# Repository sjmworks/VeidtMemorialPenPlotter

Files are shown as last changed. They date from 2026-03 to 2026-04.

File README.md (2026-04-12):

# UQ Multifunctional Composites Syringe Printer

AKA The Viedt Memorial Pen Plotter

By Sam Munro
---

The printer is heavily based upon the work of Jonathan Weiss and the Printess Bio Printer. The head is an exact rip of the Printess extruder setup attached to a fully custom gantry system.

It is suggested that you familiarise yourself with the documentation available on the [Printess GitHub](<https://github.com/weiss-jonathan/Printess-Low-Cost-3D-Printer>) before operating the VMPP.

Feel free to contact Sam - Mitch has my number
## The Printer
The bed size of the printer is 225x285mm. It has two syringe extruder heads. Each head can traverse vertically be 100mm (Z and A axes). The syringes may be depressed 50mm (B and C axes). Printess has a number of additions that can be made to the head which will work on this printer.

X and Y (multistepper in Y) are run by NEMA23 motors and TMC5160T drivers running on SPI. Vert. Axes are Alibaba NEMA17s running on TMC2209 running on UART. Control is run from an OCtopus Pro V1.1 (H723 chip).

Due to the requirement to run on the H723 chip, we are using Marlin 2.1.3-B2 which is a beta debug release of marlin. It is highly recomenned that when the stable release supports the H723 chip that the Firmware is updated to that version.

Currently the printer will home to x_max, y_max. Do not home any of the vert. axis as there are no end stops plugged it. Using sensorless homing is a possible future addition although of limited use as need to me homed manually. It is important to ensure that the vert axes will not crash when previewing the GCode. All other direction limits are software endstops so correct homing of X and Y are critical. The Octopus as 8 pins for endstops however due to the Marlin requirement of having a endstop defined for each axis it is only possible to define a min limit on one axis (one of the extra pins is used for Y2) (this may all be wrong).

The Ocotopus is running seperate power from 24V for logic and motors. The logic circuit will also be powered if you plug in the USBC. When turning on it is important to turn the main power on before connecting via USB C to avoid initialisation errors.

## Before Use and Important Notes

The printer should run both Y motors simutaneously. On occasion, often when homing has not worked properly, only one Y motor will run. If allowed this will damaged the machine. Immeadiatley switch off power (either at the wall or, if installed, on the EStop). This can be fixed by hitting the reset switch on the Octopus (above the USBC port) and rehoming.

It is imoportant to maintain lubrication of the machine both for good operation and to prevent rust. Ball screws and rails will rust if exposed. The rail carts can be lubricated by the screws on the ends. Ensure that the parts of the rails and screws that dont get oiled by movement are regularly sprayed with a lanolin or silicone grease. If parts do become rusty, gently remove with a scotch bright and then relubricate.

Before powering on the machine ensure that the Y Enstops (motor end) are equally space about 5mm from the endplates.

## Suggested Fixes and Improvements
- Estop On Motor Power Input
- The Switch on X_min is currently not used for anything other than decoration. can be wired to V pin easily.
- The Octopus Box needs a lid. DXF file is on USB or in DXF folder on CAD
- Buy and Add Feet to the machine
- 3DP a holder for the bed probe (already owned) and measure flatness of the bed. In initial testing the bed has been flat enough for small parts if you set Z at the centre of your print.
- Some of the screws don't fully engage the Nyloc (sorry). Make sure they stay tight and possibly replace.
- The Y Ball screws should probably be covered for safety
- Sensorless homing on Vertical Axes
- If a problem there is at least one spare endstop switch (V axis)
- lubricant of cart
- 3D printed box kinda sucks. Especially how the usb c doesn't fit

## Marlin and Flashing Firmware to Octopus
The Marlin file is a modified version of the one provided by Printess. Would have been easier to just start from a clean config. Feel free to improve.

The Octopus is currently setup to run over serial from Pronterface. However to flash firmware we use a MicroSD card.

Build from Marlin (ensure the printer isnt connected when building). From the PIO folder, grab firmware.bin and copy onto the SD card (delete firmware.cur if it is already in there). Plug microsd into unpowered octopus and power on over USB C. Wait for status LED to blink as standard, power off usb c and remove SD Card. The file should now be called firmware.cur. You can now power the machine over mains power and replug in the usbc to your computer after the status LED begins blinking.

## Printer Workflow
(note i am writing a lot of this from memory and bad notes after two weeks of Bintangs in Indo so some of the Gcode might be wrong)

Download Pronterface and Cura. Reread the Printess documentation.
Familiarise yourself with typical GCode and coroadinate setups (G90, G91 etc)

Turn on wall power and ensure status LED is blinking before connecting to Laptop over USB C. 

Call G28 X Y to home. Ensure that it backs off from both Y endstops after homing. If not manually move carts off endstops, reset the board via the ocotopus button and try again. ALWAYS CALL 'G28 X Y' as it will attempt to home other motors that do not have endstops if not. Call G90 to set the printer to absolute mode and call "G1 X0 Y0 F600" to send the printer to its start position

Setup Cura as described in Printess Documentation. I have included my Cura configs in the Cura folder but the settings are absolutley not dialled in for any particular reason. The most import thing is to set filament diamater to the internal diameter of your syringe and the extruder diamater to the ID of your chosen syringe. Create a STL of your part. I found it works to set the height as the expected height of the part. you made need to scale in Z in cura to get the correct amount of layers that you desire. Export the STl and bring into Cura and place as you would. Ensure the model sits flush on the build plate. Set up your parameters and slice. This will likely require a signfiicant amount of dialling in to get properties that you are happy with. good job for a RA. Export and save your GCode.

The GCode must be edited before it can be loaded into Pronterface. 
- Delete the Notes at the start
- Delete the notes at the end after the "Time Elapsed" line
- Delete the M104 bed heating commands
- Delete M107 (fans)
- Change the M82 (make sure it is M82 first) to G90. This sets it from extruder relative to total relative since we dont use extruders.
- Delete the "G1 F120 E-3" as we will do this ourselves later
- Use the Find and Replace Feature to change all the "E"s to "B"s. If using multi extruders this might be more complex sorry.

At the end of the GCode Add:
"
G91
G1 B-0.2 F100

G90
G1 Z5 F100
G1 X0 Y0 F400
"
To retract the syringe (if you deleted the extruder pullback in the direct marlin GCode) and to send the machine home

Fill the syringe enusring that no bubbles make it into the nozzle. Place the syringe into the provided holders on the machine. It may be neccessary to call "M18 B" (or other extruder axis) to disasble the stepper so that you can turn the extrusion axis by hand so that you can align the syringe holder with the plunger. Call G28 B0 after you do this. I have been doing a small initialising push in B to prime the nozzle manuallly in the pronterface terminal. If you wish you may add this to the begining of the GCode (before the G28 B0) command. I find 0.3mm of push in B is a good prepressurisation. Make sure there is a G28 B0 somewhere afterwards

Work out where in your build volume you placed the part in Cura (check the GCode against the cura preview). navigate the head to the centre of your part. Place your substrate here. You may need to lift it off the bed to ensure the nozzle can reach. used the most parralell piece of stock you can get your hands on if you need to do this. By hand rotate the Z axis until your syringe just touches the build plate. call "G28 Z0". After this point do not manually spin the Z axis. Call "G1 Z5 F200" to raise the nozzle off the build plate. You should now have set the correct Z height for your part.

When previewing the GCode it is important to preview the Min and Max values (especially for Z as it is homed by hand) to ensure the machine wont crash. go to the last extruion line and check the total change in B (or whatever extrusion axis you are using) and make sure that you fill the syringe to greater than that distance and you have sufficient leadscrew.

Have a final review of the GCode to ensure everything is within bounds and your Z never goes negative. Ensure your Feedrates are sensible. I found for printing around F400 was good. the machine will comfortably rapid X and Y at about F800. The vertical axis should not exceed F300. Test all this.

Load your GCode into the Pronterface using the "load file" button. Check everything again, especially Z heights and that you have correclty called all your G28s especially on Z. Cross your fingers and press print. Stay close to the machine and be ready to shut it down.

Goodluck and happy printing

## Other File
I have included my CAD here as well. It is a bit of a mess admititdley but I do not have Inventor on this Laptop to clean it up so my apologies. Hopefully you can make sense of it.

##

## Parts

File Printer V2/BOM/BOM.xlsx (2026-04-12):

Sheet: Sheet1
Syringe Printer Part List (sans Hardware???)
PART | QTY | MATL | SOURCE | COST PU | COST | Dims Checked? | NOTES | URL
Linear Bearing – HGH15CA | 4 |  | MAKERSTORE | 26.79 | 107.16 | x |  | https://www.makerstore.com.au/product/bear-hgh15ca/
4040 Extrusion | 0.673 |  | MAKERSTORE |  | 30.87 |  | COST IS 1M FROM MAKERSTORE (TAPPED). MANY ALT SOURCES | https://www.makerstore.com.au/product/lr-40-8-4040-s/
4080 EXTRUSION | 0.95 |  | MAKERSTORE |  | 76.04 |  | COST IS 1M FROM MAKERSTORE (TAPPED). MANY ALT SOURCES | https://www.makerstore.com.au/product/lr-40-8-4040-s/
Linear Rail – HGR15 | 0.938 |  | MAKERSTORE |  | 68.09 |  | COST IS 1M FROM MAKERSTORE MANY ALT SOURCES | https://www.makerstore.com.au/product/hard-hgr-15/
SIDE SUPPORT PLATE - MOTOR SIDE | 1 | 6MM ALY | CUT AT UQ. SOURCE ACTION? |  | 0 |  | MAY NEED TO CHANGE Z HEIGHT HERE BASED ON OTHER COMPONENTS
SIDE SUPPORT PLATE - FLOATING SIDE | 1 | 6MM ALY | CUT AT UQ |  | 0
Linear Rail Shaft Guide/SupporT – SHF12 | 4 |  | MAKERSTORE | 4.1 | 16.4 | X |  | https://www.makerstore.com.au/product/brac-shf12/
STEPPER | 3 |  | ? |  | 0 |  | CURRENTLY NEMA 23 NEEDS TO BE SPPECCED
12mm Smooth Rod | 1020 |  | MAKERSTORE | 14.96 | 29.92 |  | 2X 500MM SECTIONS. WILL BE 5MM SHORT EACH SIDE BUT SHOULD BE OK. CAN SPIN THE HOLDER TO OTHER SIDE IF NECESSARY | https://www.makerstore.com.au/product/hard-rod-12/
FF10 Floating Ball Screw Support With Clip | 3 |  | MAKERSTORE | 28.99 | 86.97 | x |  | https://www.makerstore.com.au/product/tr-bs-ff10/
FK10 Fixed Ball Screw Support With Lock Collar | 3 |  | MAKERSTORE | 28.99 | 86.97 | x |  | https://www.makerstore.com.au/product/tr-bs-fk10/
 | 3 |  | MAKERSTORE | 90.04 | 270.12 | X |  | https://www.makerstore.com.au/product/tr-bs-sfu1204/
6.35mm x 8mm Flexible Coupling | 3 |  | MAKERSTORE | 10.24 | 30.72 | x |  | https://www.makerstore.com.au/product/hard-coup-635x8/
Linear Bearing Block – 12mm – SCS12UU | 4 |  | MAKERSTORE | 6.22 | 24.88 | X |  | https://www.makerstore.com.au/product/bear-scs12uu/
DSG12H Ball Nut Housing | 1 |  | MAKERSTORE | 23.63 | 23.63 |  |  | https://www.makerstore.com.au/product/tr-bs-dsg12/
X Plate |  | 6MM ALY | CUT AT UQ |  | 0
END PLATE FIXED SIDE | 2 | 6MM ALY | CUT AT UQ |  | 0
END PLATE MOTOR SIDE | 2 | 6MM ALY | CUT AT UQ |  | 0
TOOL PLATE |  | ? |  |  | 0
ALIEXPRESS 50 AND 100MM LINEAR THINGS |  | 3DP |  |  | 0
Z AXES HOLDER | 2 | 3DP | UQ |  | 0
PLUNGER HOLDERS |  |  |  |  | 0
SYRINGES |  |  |  |  | 0
SYRINGE TIPS |  |  |  |  | 0
PSU |  |  |  |  | 0
2 Hole Corner Bracket – 40 Series | 8 |  | MAKERSTORE | 3.15 | 25.2 |  |  | https://www.makerstore.com.au/product/brac-40s-90cast-b/
 |  |  |  |  | 851.77
 |  |  |  |  | 0
 |  |  |  |  | 0
 |  |  |  |  | 0
 |  |  |  |  | 0
 |  |  |  |  | 0
 |  |  |  |  | 0
 |  |  |  |  | 0
 |  |  |  |  | 0
 |  |  |  |  | 0

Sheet: Sheet2
0.005
0.02

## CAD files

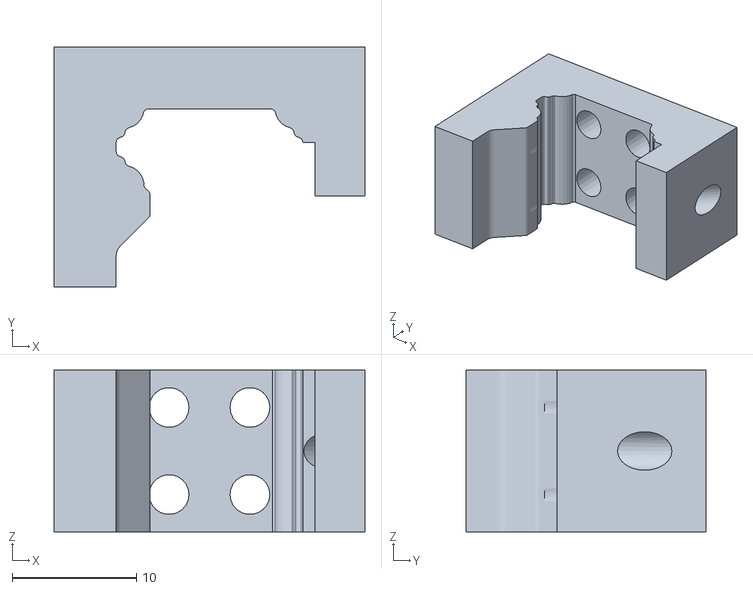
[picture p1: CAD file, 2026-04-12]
Printer V2/3D Printing/QTY4- HGR_LIMITSWITCHHOLDERv2.stl
25.0 x 19.3 x 13.0

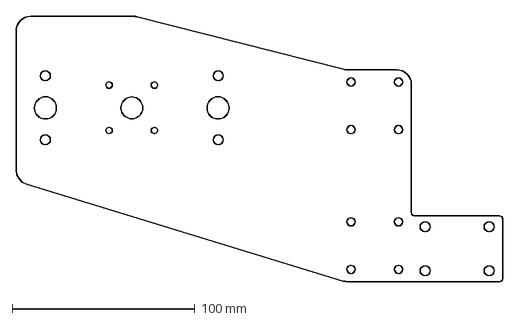
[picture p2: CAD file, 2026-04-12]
Printer V2/DWG/LASER CUTTING - DXFS/QTY 1 - SIDE SUPPORT PLATE - PASSIVE SIDE.dxf
266.0 x 145.0 mm

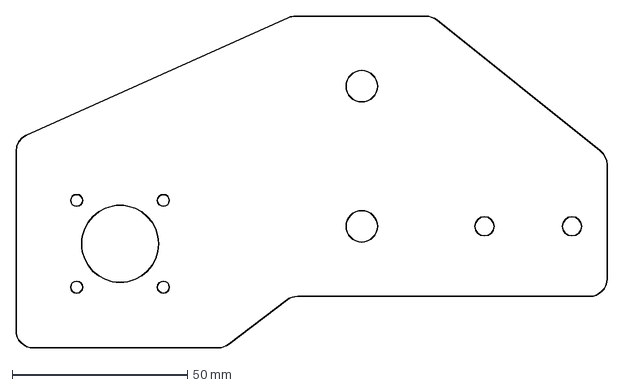
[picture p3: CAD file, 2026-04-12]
Printer V2/DWG/LASER CUTTING - FOR QUOTE/LASER CUTTING - DXFS/QTY 2 - ENDPLATE - PASSIVE SIDE.dxf
168.7 x 94.7 mm

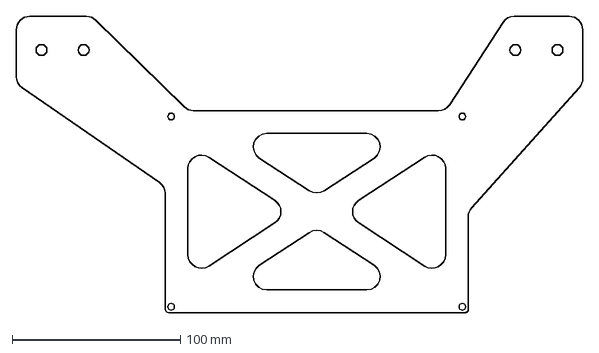
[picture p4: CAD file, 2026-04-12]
Printer V2/DXFS/ocotpous_box_backing plate.dxf
336.5 x 176.0 mm

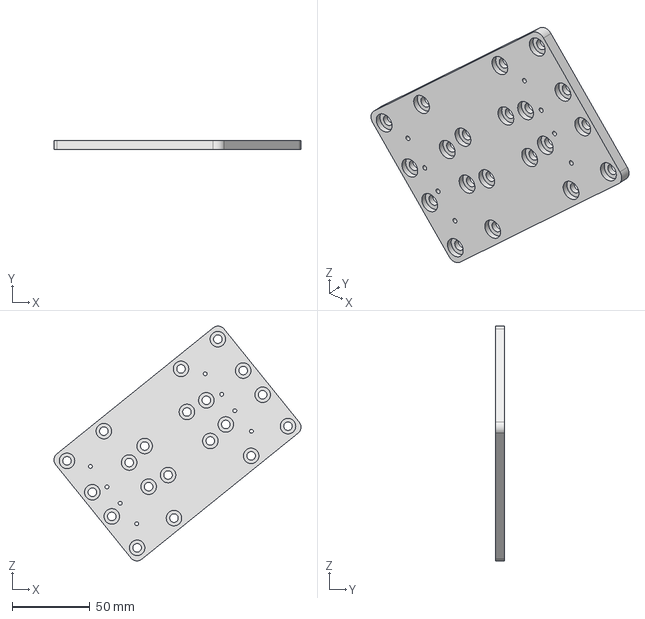
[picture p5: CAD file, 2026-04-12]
Printer V2/FOR MACHINING/X_PLATE.stp
159.2 x 6.00 x 151.3 mm

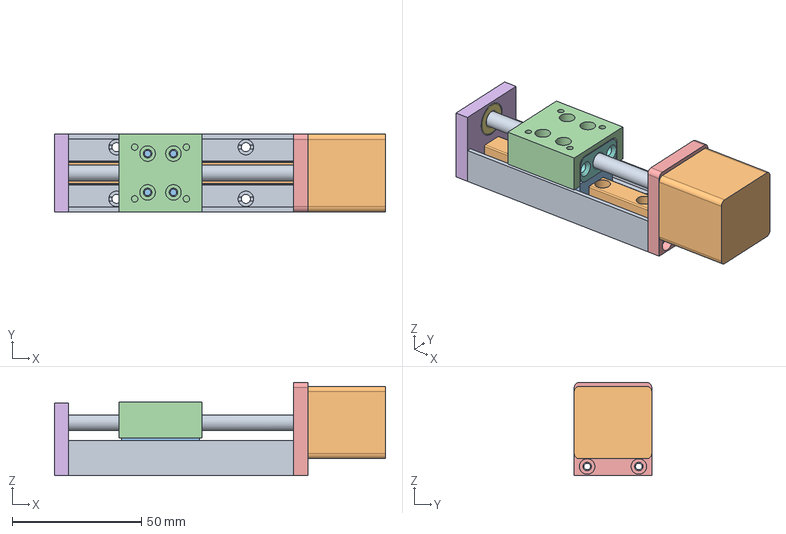
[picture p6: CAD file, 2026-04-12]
Printer V2/PRINTESS FILES/DG281-50L .stp
128.0 x 30.0 x 36.0 mm

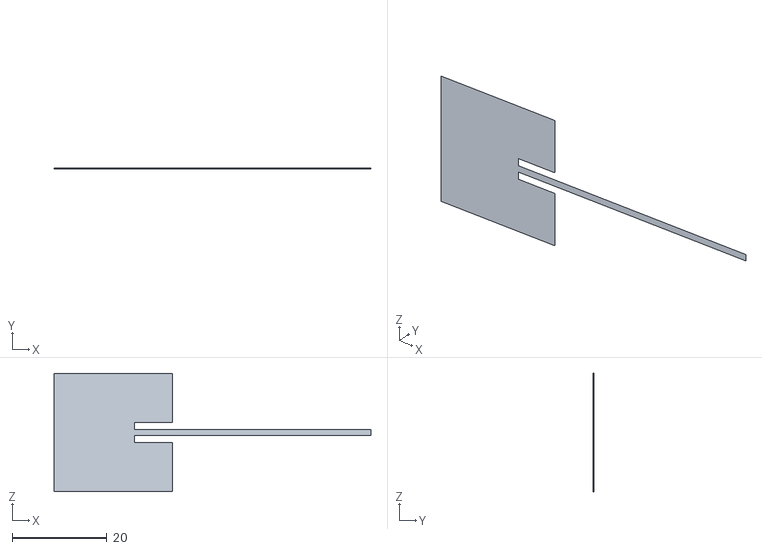
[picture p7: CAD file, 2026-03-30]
Printer V2/PRINTING FILES/TESTPRINT1_1.stl
67.0 x 0.1 x 25.0

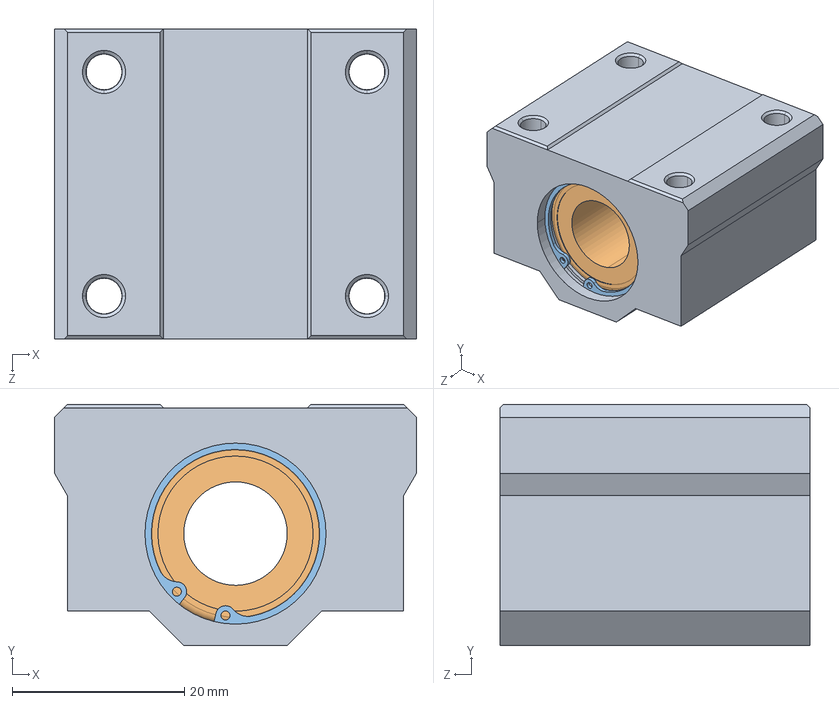
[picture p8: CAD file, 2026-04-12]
Printer V2/SCS12UU.STEP
42.0 x 28.0 x 36.0 mm
3_PreviewCfg x 2

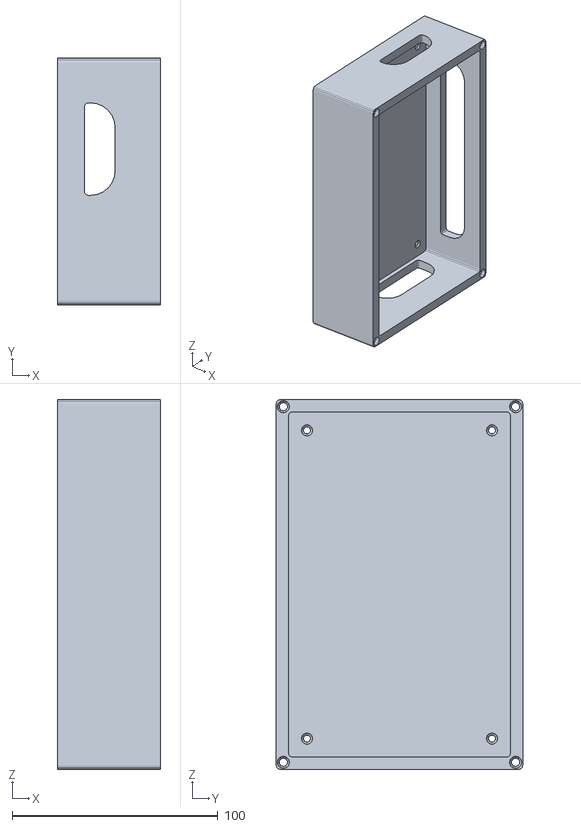
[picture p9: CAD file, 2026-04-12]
Printer V2/3D Printing/OCTOPUS_BOX.stl
50.0 x 120.0 x 180.0

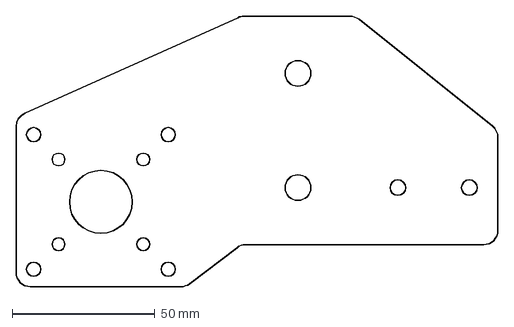
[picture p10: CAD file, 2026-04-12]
Printer V2/DWG/LASER CUTTING - DXFS/QTY 2 - ENDPLATE - MOTOR SIDE.dxf
168.7 x 94.7 mm

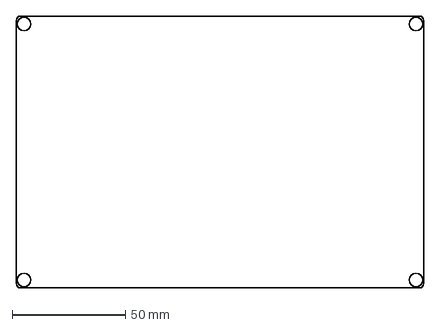
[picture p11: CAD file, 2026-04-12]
Printer V2/DXFS/ocotppusbox lid.dxf
180.0 x 120.0 mm

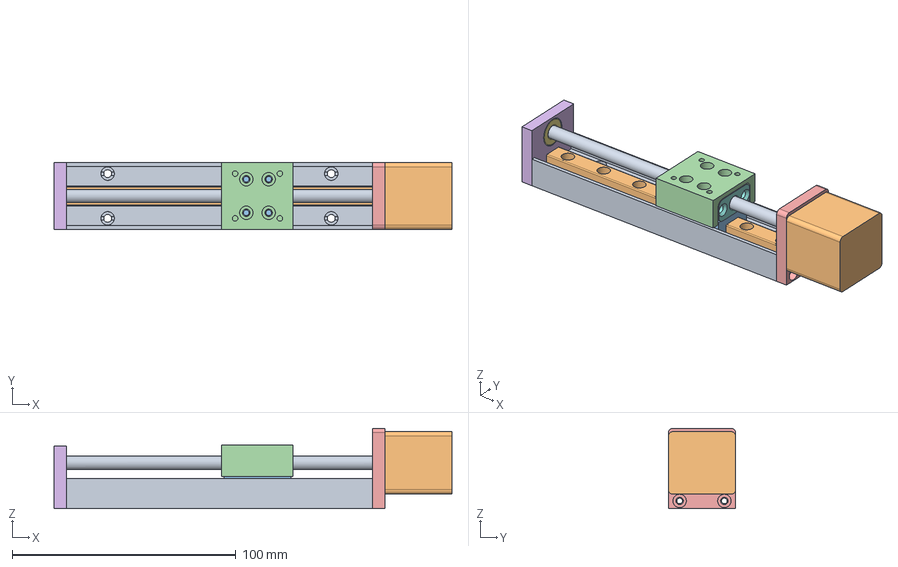
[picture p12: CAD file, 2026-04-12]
Printer V2/PRINTESS FILES/DG281-100L .stp
178.0 x 30.0 x 36.0 mm

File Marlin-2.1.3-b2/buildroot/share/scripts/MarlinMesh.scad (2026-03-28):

 /**************************************\
 *                                      *
 *   OpenSCAD Mesh Display              *
 *   by Thinkyhead - April 2017         *
 *                                      *
 *   Copy the grid output from Marlin,  *
 *   paste below as shown, and use      *
 *   OpenSCAD to see a visualization    *
 *   of your mesh.                      *
 *                                      *
 \**************************************/

$t = 0.15; // comment out during animation!
X = 0; Y = 1;
L = 0; R = 1; F = 2; B = 3;

//
// Sample Mesh - Replace with your own
//
measured_z = [
  [ -1.20, -1.13, -1.09, -1.03, -1.19 ],
  [ -1.16, -1.25, -1.27, -1.25, -1.08 ],
  [ -1.13, -1.26, -1.39, -1.31, -1.18 ],
  [ -1.09, -1.20, -1.26, -1.21, -1.18 ],
  [ -1.13, -0.99, -1.03, -1.06, -1.32 ]
];

//
// An offset to add to all points in the mesh
//
zadjust     = 0;

//
// Mesh characteristics
//
bed_size = [ 200, 200 ];

mesh_inset  = [ 10, 10, 10, 10 ]; // L, F, R, B

mesh_bounds = [
  [ mesh_inset[L], mesh_inset[F] ],
  [ bed_size[X] - mesh_inset[R], bed_size[Y] - mesh_inset[B] ]
];

mesh_size = mesh_bounds[1] - mesh_bounds[0];

                      // NOTE: Marlin meshes already subtract the probe offset
NAN         = 0;      // Z to use for un-measured points

//
// Geometry
//

max_z_scale   = 100;   // Scale at Time 0.5
min_z_scale   = 10;    // Scale at Time 0.0 and 1.0
thickness     = 0.5;   // thickness of the mesh triangles
tesselation   = 1;     // levels of tesselation from 0-2
alternation   = 2;     // direction change modulus (try it)

//
// Appearance
//

show_plane    = true;
show_labels   = true;
show_coords   = true;
arrow_length  = 5;

label_font_lg = "Arial";
label_font_sm = "Arial";
mesh_color    = [1,1,1,0.5];
plane_color   = [0.4,0.6,0.9,0.6];

//================================================ Derive useful values

big_z = max_2D(measured_z,0);
lil_z = min_2D(measured_z,0);

mean_value = (big_z + lil_z) / 2.0;

mesh_points_y = len(measured_z);
mesh_points_x = len(measured_z[0]);

xspace = mesh_size[X] / (mesh_points_x - 1);
yspace = mesh_size[Y] / (mesh_points_y - 1);

// At $t=0 and $t=1 scale will be 100%
z_scale_factor = min_z_scale + (($t > 0.5) ? 1.0 - $t : $t) * (max_z_scale - min_z_scale) * 2;

//
// Min and max recursive functions for 1D and 2D arrays
// Return the smallest or largest value in the array
//
function some_1D(b,i) = (i<len(b)-1) ? (b[i] && some_1D(b,i+1)) : b[i] != 0;
function some_2D(a,j) = (j<len(a)-1) ? some_2D(a,j+1) : some_1D(a[j], 0);
function min_1D(b,i) = (i<len(b)-1) ? min(b[i], min_1D(b,i+1)) : b[i];
function min_2D(a,j) = (j<len(a)-1) ? min_2D(a,j+1) : min_1D(a[j], 0);
function max_1D(b,i) = (i<len(b)-1) ? max(b[i], max_1D(b,i+1)) : b[i];
function max_2D(a,j) = (j<len(a)-1) ? max_2D(a,j+1) : max_1D(a[j], 0);

//
// Get the corner probe points of a grid square.
//
// Input  : x,y grid indexes
// Output : An array of the 4 corner points
//
function grid_square(x,y) = [
  [x * xspace, y * yspace, z_scale_factor * (measured_z[y][x] - mean_value)],
  [x * xspace, (y+1) * yspace, z_scale_factor * (measured_z[y+1][x] - mean_value)],
  [(x+1) * xspace, (y+1) * yspace, z_scale_factor * (measured_z[y+1][x+1] - mean_value)],
  [(x+1) * xspace, y * yspace, z_scale_factor * (measured_z[y][x+1] - mean_value)]
];

// The corner point of a grid square with Z centered on the mean
function pos(x,y,z) = [x * xspace, y * yspace, z_scale_factor * (z - mean_value)];

//
// Draw the point markers and labels
//
module point_markers(show_home=true) {
  // Mark the home position 0,0
  if (show_home)
    translate([1,1]) color([0,0,0,0.25])
      cylinder(r=1, h=z_scale_factor, center=true);

  for (x=[0:mesh_points_x-1], y=[0:mesh_points_y-1]) {
    z = measured_z[y][x] - zadjust;
    down = z < mean_value;
    xyz = pos(x, y, z);
    translate([ xyz[0], xyz[1] ]) {

      // Show the XY as well as the Z!
      if (show_coords) {
        color("black")
        translate([0,0,0.5]) {
          $fn=8;
          rotate([0,0]) {
            posx = floor(mesh_bounds[0][X] + x * xspace);
            posy = floor(mesh_bounds[0][Y] + y * yspace);
            text(str(posx, ",", posy), 2, label_font_sm, halign="center", valign="center");
          }
        }
      }

      translate([ 0, 0, xyz[2] ]) {
        // Label each point with the Z
        v = z - mean_value;
        if (show_labels) {

          color(abs(v) < 0.1 ? [0,0.5,0] : [0.25,0,0])
          translate([0,0,down?-10:10]) {

            $fn=8;
            rotate([90,0])
              text(str(z), 6, label_font_lg, halign="center", valign="center");

            if (v)
              translate([0,0,down?-6:6]) rotate([90,0])
                text(str(down || !v ? "" : "+", v), 3, label_font_sm, halign="center", valign="center");
          }
        }

        // Show an arrow pointing up or down
        if (v) {
          rotate([0, down ? 180 : 0]) translate([0,0,-1])
            cylinder(
              r1=0.5,
              r2=0.1,
              h=arrow_length, $fn=12, center=1
            );
        }
        else
          color([1,0,1,0.4]) sphere(r=1.0, $fn=20, center=1);
      }
    }
  }
}

//
// Split a square on the diagonal into
// two triangles and render them.
//
//     s : a square
//   alt : a flag to split on the other diagonal
//
module tesselated_square(s, alt=false) {
  add = [0,0,thickness];
  p1 = [
    s[0], s[1], s[2], s[3],
    s[0]+add, s[1]+add, s[2]+add, s[3]+add
  ];
  f1 = alt
      ? [ [0,1,3], [4,5,1,0], [4,7,5], [5,7,3,1], [7,4,0,3] ]
      : [ [0,1,2], [4,5,1,0], [4,6,5], [5,6,2,1], [6,4,0,2] ];
  f2 = alt
      ? [ [1,2,3], [5,6,2,1], [5,6,7], [6,7,3,2], [7,5,1,3] ]
      : [ [0,2,3], [4,6,2,0], [4,7,6], [6,7,3,2], [7,4,0,3] ];

  // Use the other diagonal
  polyhedron(points=p1, faces=f1);
  polyhedron(points=p1, faces=f2);
}

/**
 * The simplest mesh display
 */
module simple_mesh(show_plane=show_plane) {
  if (show_plane) color(plane_color) cube([mesh_size[X], mesh_size[Y], thickness]);
  color(mesh_color)
    for (x=[0:mesh_points_x-2], y=[0:mesh_points_y-2])
      tesselated_square(grid_square(x, y));
}

/**
 * Subdivide the mesh into smaller squares.
 */
module bilinear_mesh(show_plane=show_plane,tesselation=tesselation) {
  if (show_plane) color(plane_color) translate([-5,-5]) cube([mesh_size[X]+10, mesh_size[Y]+10, thickness]);

  if (some_2D(measured_z, 0)) {

    tesselation = tesselation % 4;
    color(mesh_color)
    for (x=[0:mesh_points_x-2], y=[0:mesh_points_y-2]) {
      square = grid_square(x, y);
      if (tesselation < 1) {
        tesselated_square(square,(x%alternation)-(y%alternation));
      }
      else {
        subdiv_4 = subdivided_square(square);
        if (tesselation < 2) {
          for (i=[0:3]) tesselated_square(subdiv_4[i],i%alternation);
        }
        else {
          for (i=[0:3]) {
            subdiv_16 = subdivided_square(subdiv_4[i]);
            if (tesselation < 3) {
              for (j=[0:3]) tesselated_square(subdiv_16[j],j%alternation);
            }
            else {
              for (j=[0:3]) {
                subdiv_64 = subdivided_square(subdiv_16[j]);
                if (tesselation < 4) {
                  for (k=[0:3]) tesselated_square(subdiv_64[k]);
                }
              }
            }
          }
        }
      }
    }

  }
}

//
// Subdivision helpers
//
function ctrz(a) = (a[0][2]+a[1][2]+a[3][2]+a[2][2])/4;
function avgx(a,i) = (a[i][0]+a[(i+1)%4][0])/2;
function avgy(a,i) = (a[i][1]+a[(i+1)%4][1])/2;
function avgz(a,i) = (a[i][2]+a[(i+1)%4][2])/2;

//
// Convert one square into 4, applying bilinear averaging
//
// Input  : 1 square (4 points)
// Output : An array of 4 squares
//
function subdivided_square(a) = [
  [ // SW square
    a[0],                          // SW
    [a[0][0],avgy(a,0),avgz(a,0)], // CW
    [avgx(a,1),avgy(a,0),ctrz(a)], // CC
    [avgx(a,1),a[0][1],avgz(a,3)]  // SC
  ],
  [ // NW square
    [a[0][0],avgy(a,0),avgz(a,0)], // CW
    a[1],                          // NW
    [avgx(a,1),a[1][1],avgz(a,1)], // NC
    [avgx(a,1),avgy(a,0),ctrz(a)]  // CC
  ],
  [ // NE square
    [avgx(a,1),avgy(a,0),ctrz(a)], // CC
    [avgx(a,1),a[1][1],avgz(a,1)], // NC
    a[2],                          // NE
    [a[2][0],avgy(a,0),avgz(a,2)]  // CE
  ],
  [ // SE square
    [avgx(a,1),a[0][1],avgz(a,3)], // SC
    [avgx(a,1),avgy(a,0),ctrz(a)], // CC
    [a[2][0],avgy(a,0),avgz(a,2)], // CE
    a[3]                           // SE
  ]
];


//================================================ Run the plan

translate([-mesh_size[X] / 2, -mesh_size[Y] / 2]) {
  $fn = 12;
  point_markers();
  bilinear_mesh();
}

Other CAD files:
Printer V2/DWG/ENDPLATES - DWG.dwg
Printer V2/DWG/UQ Composites - Sami.dwg
Printer V2/FOR MACHINING/X PLATE - DWG.dwg
Printer V2/PRINTING FILES/TESTPRINT1.stl
Printer V2/12MM_X_AXIS_SHAFT.ipt
Printer V2/178202343-9-stepper_am23hs0420-01/OldVersions/stepper_am23hs0420-01.0001.iam
Printer V2/178202343-9-stepper_am23hs0420-01/OldVersions/stepper_am23hs0420-01_01.0001.ipt
Printer V2/178202343-9-stepper_am23hs0420-01/OldVersions/stepper_am23hs0420-01_02.0001.ipt
Printer V2/178202343-9-stepper_am23hs0420-01/stepper_am23hs0420-01.iam
Printer V2/178202343-9-stepper_am23hs0420-01/stepper_am23hs0420-01_01.ipt
Printer V2/178202343-9-stepper_am23hs0420-01/stepper_am23hs0420-01_02.ipt
Printer V2/3D Printing/QTY 2 1mL Barrel Holder.stl
Printer V2/3D Printing/QTY 2 1mL Plunger Holder.stl
Printer V2/3D Printing/QTY 2 5mL BD Plunger Holder.stl
Printer V2/3D Printing/QTY 2 5mL Barrel Holder.stl
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

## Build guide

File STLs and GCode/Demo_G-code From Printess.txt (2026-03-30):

; Demo GCode for a 2-syringe multimaterial print.

; Clear Nozzle Extrusion Coefficient = 2
G90 ; Absolute mode
G21 ; Set units to mm

; Manually position all axes to desired starting position. Bring nozzles so that they just barely make contact with the stage

G1 X0 Y0 Z2 A2 F300 ; Move nozzles up so they don't crash into the print
G1 Z0.05 F200 ; Move Z nozzle up a defined height for extrusion. ADJUST IF NECESSARY

;;;;;;;;;;;;;;;;;;;;;;;;;;;;;;;;;;;;;;;;;;;;;;;;;;;;;;;;;;;;;;;;;;;;;;;;;;;;;;
G91; Relative mode
G1 B0.1 F200 ; WRITE IN the initial distance to pressurize the syringe
G92 B0; Set extruder position to 0 after initial pressurization
;;;;;;;;;;;;;;;;;;;;;;;;;;;;;;;;;;;;;;;;;;;;;;;;;;;;;;;;;;;;;;;;;;;;;;;;;;;;;;

G90 ; absolute mode

G1 X5.3 Y0.0 B0.025 F300.0
G1 X5.3 Y0.5 B0.027 F300.0
G1 X0.0 Y0.5 B0.052 F300.0
G1 X0.0 Y1.0 B0.055 F300.0
G1 X5.3 Y1.0 B0.08 F300.0
G1 X5.3 Y1.5 B0.082 F300.0
G1 X0.0 Y1.5 B0.107 F300.0
G1 X0.0 Y2.0 B0.11 F300.0
G1 X5.3 Y2.0 B0.135 F300.0
G1 X5.3 Y2.5 B0.137 F300.0
G1 X0.0 Y2.5 B0.162 F300.0
G1 X0.0 Y3.0 B0.164 F300.0
G1 X5.3 Y3.0 B0.19 F300.0
G1 X5.3 Y3.5 B0.192 F300.0
G1 X0.0 Y3.5 B0.217 F300.0
G1 X0.0 Y4.0 B0.219 F300.0
G1 X5.3 Y4.0 B0.244 F300.0
G1 X5.3 Y4.5 B0.247 F300.0
G1 X0.0 Y4.5 B0.272 F300.0
G1 X0.0 Y5.0 B0.274 F300.0
G1 X5.3 Y5.0 B0.299 F300.0

;;;;;;;;;;;;;;;;;;;;;;;;;;;;;;;;;;;;;;;;;;;;;;;;;;;;;;;;;;;;;;;;;;;;;;;;;;;;;;
G91
G1 B-0.1 F200; WRITE in the distance to depressurize the syringe
G92 B0 ; Reset Extruder to 0
;;;;;;;;;;;;;;;;;;;;;;;;;;;;;;;;;;;;;;;;;;;;;;;;;;;;;;;;;;;;;;;;;;;;;;;;;;;;;;

G90
G1 Z1.0 F300.0; Raise Z to get out of the way of the print.

;;;;;;;;;;;;;;;Adjust for X/Y Offset between plungers;;;;;;;;;;;;;;
G91
G1 X32.67 Y0.55 F300.0
G92 X0 Y0
;;;;;;;;;;;;;;;;;;;;;;;;;;;;;;;;;;;;;;;;;;;;;;;;;;;;;;;;;;;;;;;;;;;

G90
G1 X0 Y0 A0.05 F300; Bring A axis down

;;;;;;;;;;;;;;;;;;;;;;;;;;;;;;;;;;;;;;;;;;;;;;;;;;;;;;;;;;;;;;;;;;;;;;;;;;;;;;
G91
G1 C0.1 F200 ; WRITE IN the distance to pressurize the syringe 
G92 C0 ; DEFINE EXTRUDER POSITION TO MATCH THE BEGINNING OF THE EXTRUSION VALUES BELOW
;;;;;;;;;;;;;;;;;;;;;;;;;;;;;;;;;;;;;;;;;;;;;;;;;;;;;;;;;;;;;;;;;;;;;;;;;;;;;;

G90

G1 X0.0 Y-5.1 C0.024 F300.0
G1 X-0.5 Y-5.1 C0.026 F300.0
G1 X-0.5 Y0.0 C0.051 F300.0
G1 X-1.0 Y0.0 C0.053 F300.0
G1 X-1.0 Y-5.1 C0.077 F300.0
G1 X-1.5 Y-5.1 C0.079 F300.0
G1 X-1.5 Y0.0 C0.103 F300.0
G1 X-2.0 Y0.0 C0.106 F300.0
G1 X-2.0 Y-5.1 C0.13 F300.0
G1 X-2.5 Y-5.1 C0.132 F300.0
G1 X-2.5 Y0.0 C0.156 F300.0
G1 X-3.0 Y0.0 C0.159 F300.0
G1 X-3.0 Y-5.1 C0.183 F300.0
G1 X-3.5 Y-5.1 C0.185 F300.0
G1 X-3.5 Y0.0 C0.209 F300.0
G1 X-4.0 Y0.0 C0.212 F300.0
G1 X-4.0 Y-5.1 C0.236 F300.0
G1 X-4.5 Y-5.1 C0.238 F300.0
G1 X-4.5 Y0.0 C0.262 F300.0
G1 X-5.0 Y0.0 C0.265 F300.0
G1 X-5.0 Y-5.1 C0.289 F300.0

;;;;;;;;;;;;;;;;;;;;;;;;;;;;;;;;;;;;;;;;;;;;;;;;;;;;;;;;;;;;;;;;;;;;;;;;;;;;;;
G91
G1 C-0.1 F200; WRITE IN the distance to depressurize the syringe
;;;;;;;;;;;;;;;;;;;;;;;;;;;;;;;;;;;;;;;;;;;;;;;;;;;;;;;;;;;;;;;;;;;;;;;;;;;;;;

G90
G1 X-40 Y-5.1 Z10 A10 F300
G92 X0 Y0 Z10 A10 ;Reset coordinates ready for next print to the side

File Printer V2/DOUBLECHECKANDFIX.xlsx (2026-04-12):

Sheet: Sheet1
QUESTIONS TO FIX DON’T FORGET | NOTES | CHECKED?
ACTUAL BASE DIMESNIONS | WILL BE DRIVEN BY GANTRY AND PART OVERHANGS TO HIT TARGET WORKSIZE
ROUIND SHAFT MOUNTAIN HOLES SEP DIST | CURRENTLY SIZED FOR THE MAKERSTORE PARTS
NEMA MOTOR MOUNTINA HOLE SPACING
CENTRE HOLE FOR BALL SCREW MOUNTINA
MIUNTAIN PLATE FORWARD AND BACK DIST
CART DEPERATION
NEMA SIZING
LINEAR SHAFT HOLE SIZE FOR CUTTING
THICKNESS OF ENDPLATES
z HEIGHT | MITCH QUESTION
TYPE AND QUAlity of linear BEARING BLOCK
FROM ABOVE - HOLE SIZING
YAXIS CART HOLE SIZING
YAXIS CARTS MATCH PURCHASED UNITS
MOUNT FIXED END ON INSIDE OR OUTSIDE
SPEC MOTORS
X MOTOR STANDOFF DISTANCE
RPD END TINGS ARE NOT TO SPEC OF MAKERSTORE
Limit switches
OUTBOARDSPACING OF Y SCREW
STANDOFF Y AXIS FK TO ADD PLAY |  |  |  | 23
Holes in rail
 |  |  | 960
https://kiwimotion.co.uk/technical-articles/ball-screws/ball-screw-selection/ |  |  | 640
https://m.media-amazon.com/images/I/71zBOVmqRrL._UF1000,1000_QL80_.jpg |  |  | 436

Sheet: CALCS
4080 |  |  | 12MM ROD
sa | 15.332 | CM2 | SA | 1.130973355 | CM2
VOL/M | 1533.2 | CM3 | VOL/M | 113.0973355 | CM3
DENSITY | 2.7 | G/CM3 | DENSITY | 7.8 | G/CM3
MASS/M | 4139.64 | G | MASS/M | 882.1592171 | G/CM3
2040
sa | 2.75
VOL/M | 275
DENSITY | 2.7
MASS/M | 742.5

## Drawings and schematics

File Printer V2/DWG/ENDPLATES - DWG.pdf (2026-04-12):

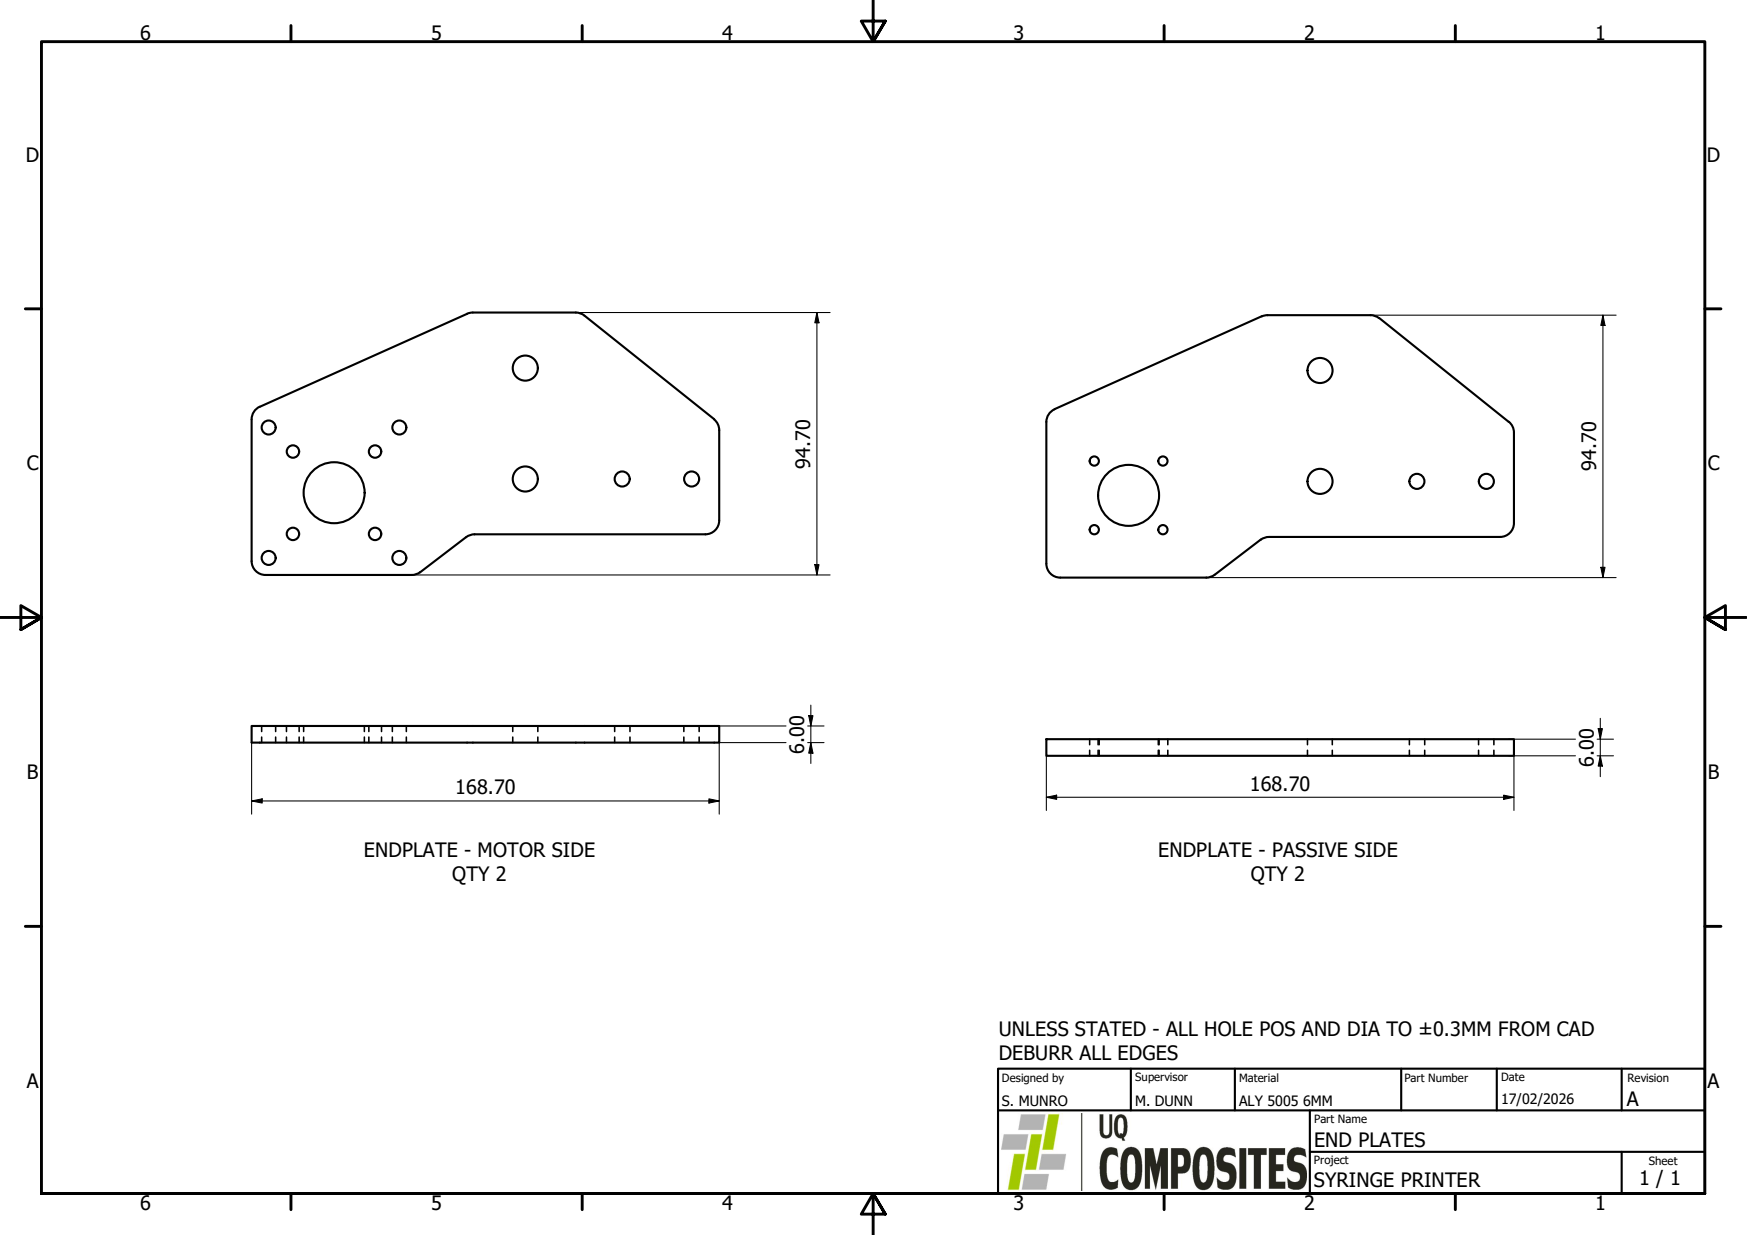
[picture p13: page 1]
QTY 2

ENDPLATE - MOTOR SIDE

ENDPLATE - PASSIVE SIDE

UNLESS STATED - ALL HOLE POS AND DIA TO ±0.3MM FROM CAD
DEBURR ALL EDGES

Designed by S. MUNRO | Supervisor M. DUNN | Material ALY 5005 6MM | Part Number | Date 17/02/2026 | Revision A

Part Name END PLATES

Project SYRINGE PRINTER | Sheet 1 / 1

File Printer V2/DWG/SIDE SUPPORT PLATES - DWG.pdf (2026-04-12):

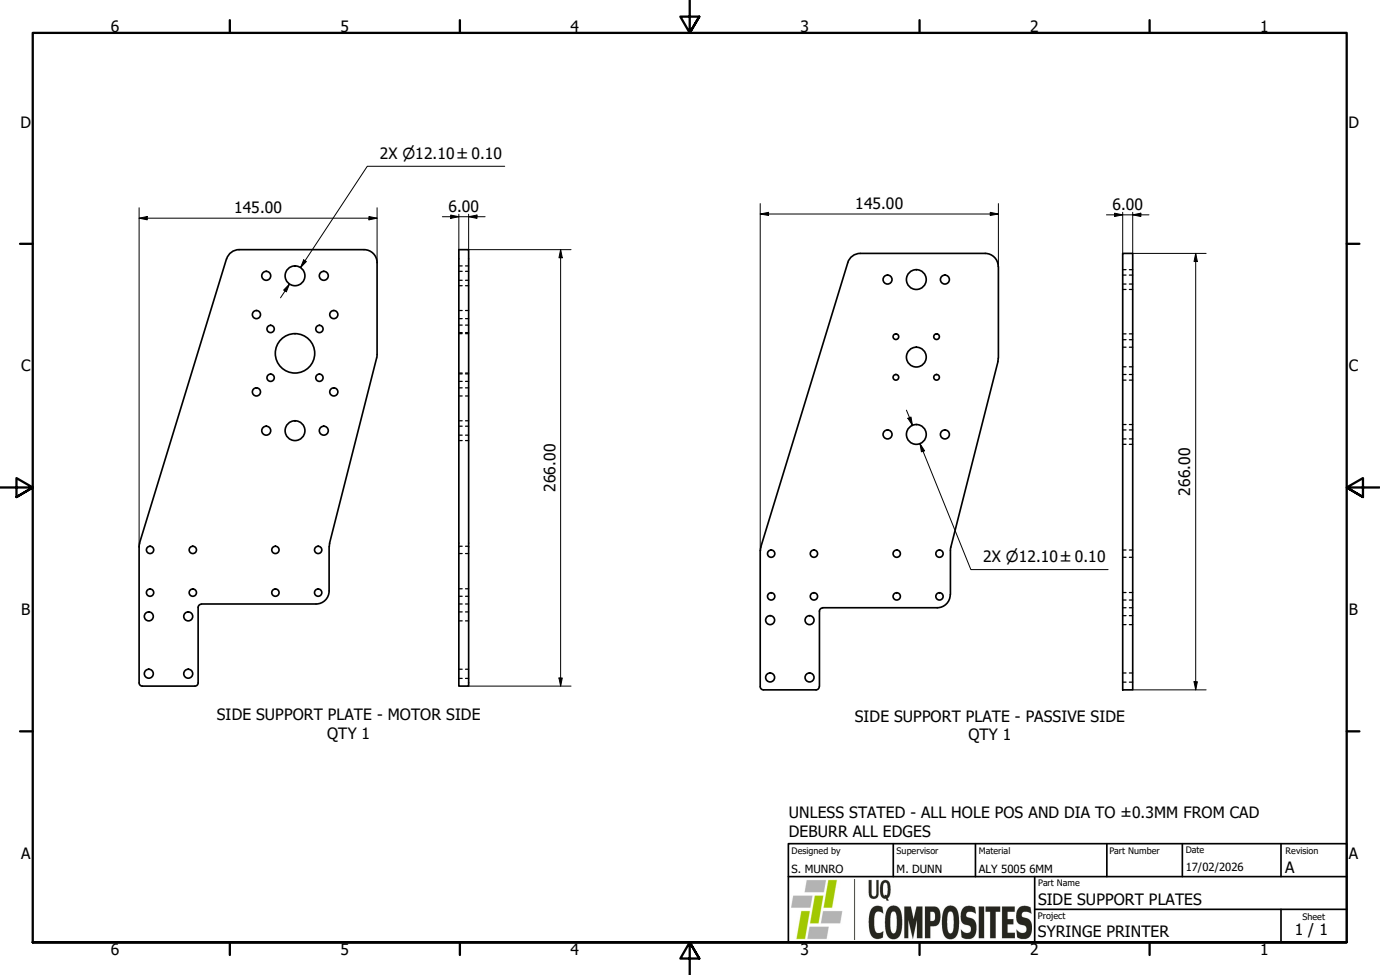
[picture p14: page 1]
QTY 1

SIDE SUPPORT PLATE - MOTOR SIDE

SIDE SUPPORT PLATE - PASSIVE SIDE

UNLESS STATED - ALL HOLE POS AND DIA TO ±0.3MM FROM CAD
DEBURR ALL EDGES

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

Part Name SIDE SUPPORT PLATES

Project SYRINGE PRINTER | Sheet 1 / 1

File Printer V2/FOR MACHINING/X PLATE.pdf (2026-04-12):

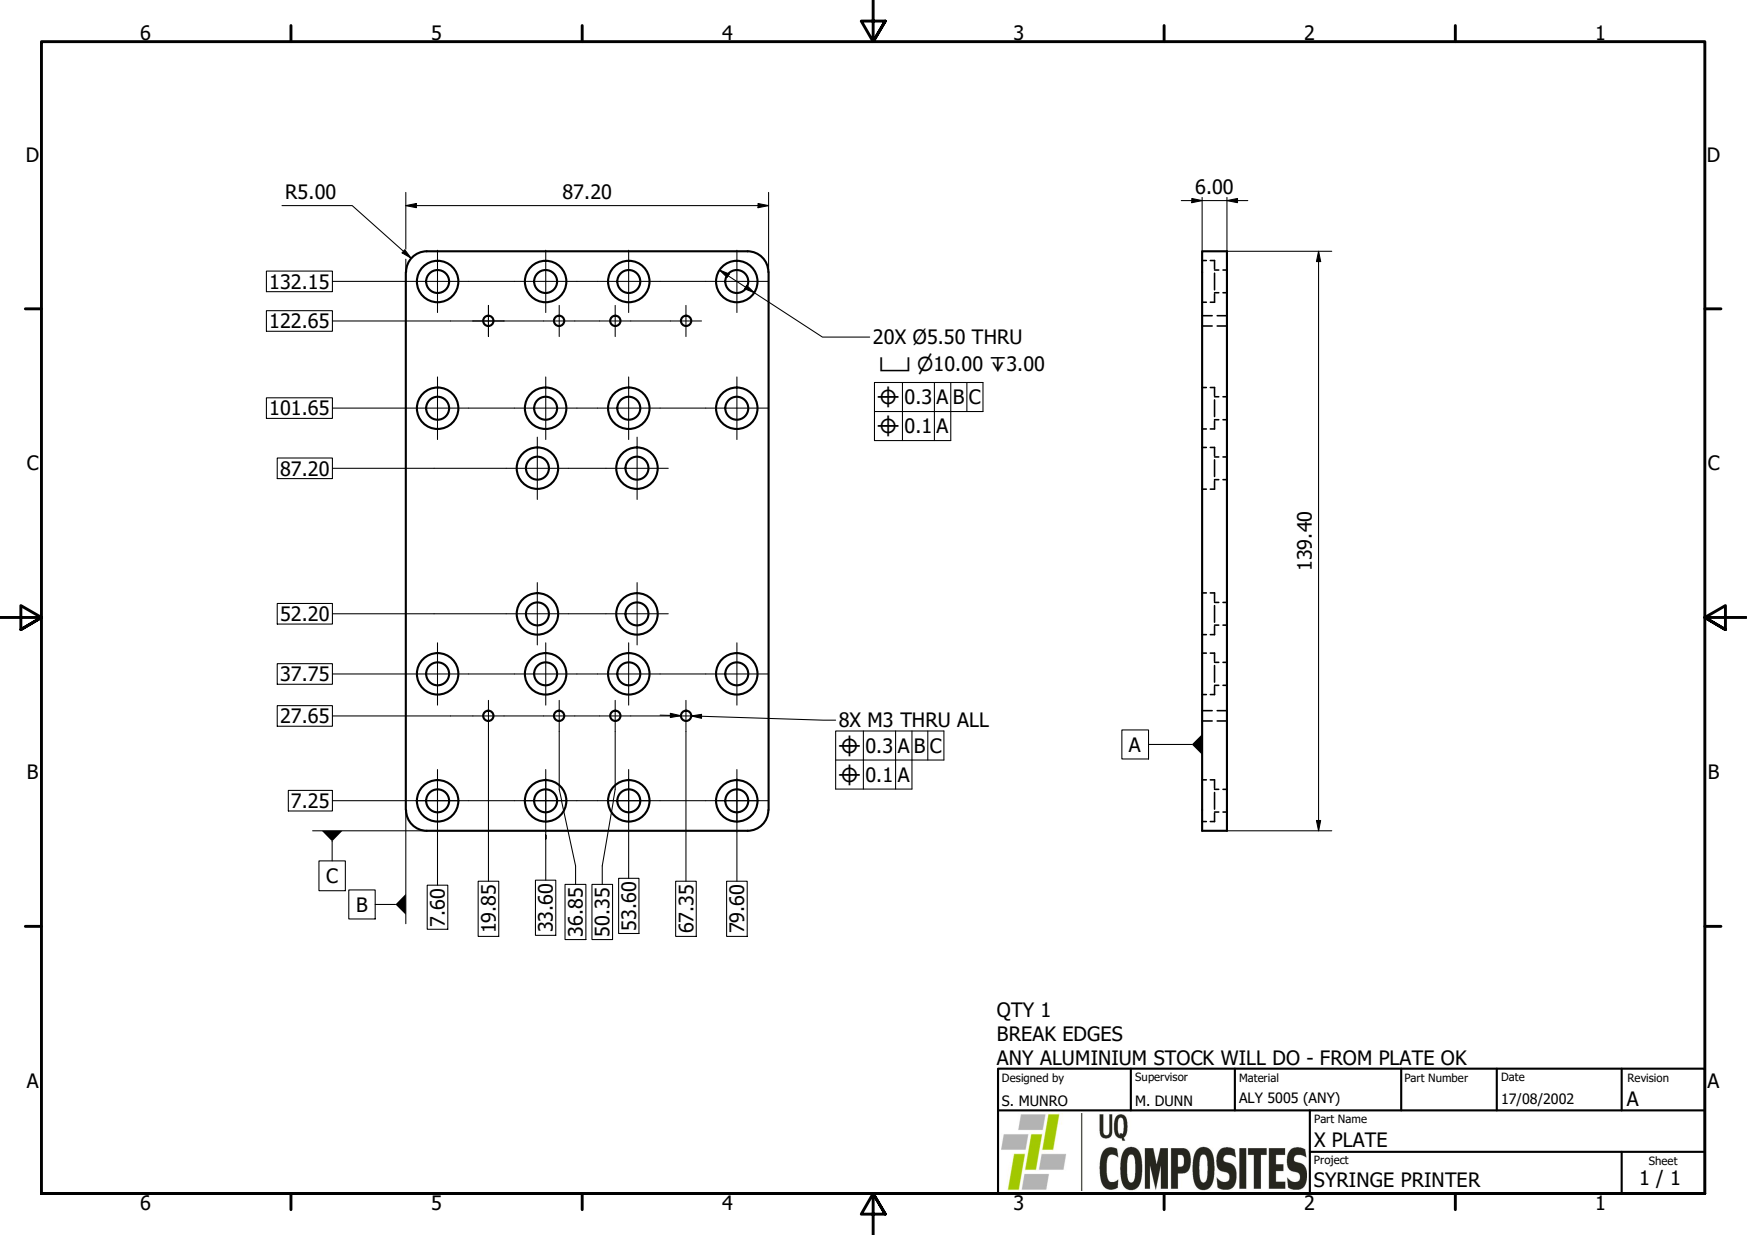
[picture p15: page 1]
20X Ø5.50 THRU; 8X M3 THRU ALL ⌖ 0.3 A B C

⌖ 0.3 A B C
⌖ 0.1 A

QTY 1
BREAK EDGES
ANY ALUMINIUM STOCK WILL DO - FROM PLATE OK

Designed by S. MUNRO | Supervisor M. DUNN | Material ALY 5005 (ANY) | Part Number | Date 17/08/2002 | Revision A

Part Name X PLATE

Project SYRINGE PRINTER | Sheet 1 / 1

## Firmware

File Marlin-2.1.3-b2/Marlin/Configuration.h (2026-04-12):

/**
 * Marlin 3D Printer Firmware
 * Copyright (c) 2020 MarlinFirmware [https://github.com/MarlinFirmware/Marlin]
 *
 * Based on Sprinter and grbl.
 * Copyright (c) 2011 Camiel Gubbels / Erik van der Zalm
 *
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
 */
#pragma once

/**
 * Configuration.h
 *
 * Basic settings such as:
 *
 * - Type of electronics
 * - Type of temperature sensor
 * - Printer geometry
 * - Endstop configuration
 * - LCD controller
 * - Extra features
 *
 * Advanced settings can be found in Configuration_adv.h
 */
#define CONFIGURATION_H_VERSION 02010300

//===========================================================================
//============================= Getting Started =============================
//===========================================================================

/**
 * Here are some useful links to help get your machine configured and calibrated:
 *
 * Example Configs:     https://github.com/MarlinFirmware/Configurations/branches/all
 *
 * Průša Calculator:    https://blog.prusa3d.com/calculator_3416/
 *
 * Calibration Guides:  https://reprap.org/wiki/Calibration
 *                      https://reprap.org/wiki/Triffid_Hunter%27s_Calibration_Guide
 *                      https://web.archive.org/web/20220907014303/sites.google.com/site/repraplogphase/calibration-of-your-reprap
 *                      https://youtu.be/wAL9d7FgInk
 *                      https://teachingtechyt.github.io/calibration.html
 *
 * Calibration Objects: https://www.thingiverse.com/thing:5573
 *                      https://www.thingiverse.com/thing:1278865
 */

// @section info

// Author info of this build printed to the host during boot and M115
#define STRING_CONFIG_H_AUTHOR "(none, default config)" // Original author or contributor.
//#define CUSTOM_VERSION_FILE Version.h // Path from the root directory (no quotes)

// @section machine

// Choose the name from boards.h that matches your setup
#ifndef MOTHERBOARD
  #define MOTHERBOARD BOARD_BTT_OCTOPUS_PRO_V1_1
#endif

// @section serial

/**
 * Select the serial port on the board to use for communication with the host.
 * This allows the connection of wireless adapters (for instance) to non-default port pins.
 * Serial port -1 is the USB emulated serial port, if available.
 * Note: The first serial port (-1 or 0) will always be used by the Arduino bootloader.
 *
 * :[-1, 0, 1, 2, 3, 4, 5, 6, 7, 8, 9]
 */
#define SERIAL_PORT -1

/**
 * Serial Port Baud Rate
 * This is the default communication speed for all serial ports.
 * Set the baud rate defaults for additional serial ports below.
 *
 * 250000 works in most cases, but you might try a lower speed if
 * you commonly experience drop-outs during host printing.
 * You may try up to 1000000 to speed up SD file transfer.
 *
 * :[2400, 9600, 19200, 38400, 57600, 115200, 250000, 500000, 1000000]
 */
#define BAUDRATE 115200

//#define BAUD_RATE_GCODE     // Enable G-code M575 to set the baud rate

/**
 * Select a secondary serial port on the board to use for communication with the host.
 * Currently Ethernet (-2) is only supported on Teensy 4.1 boards.
 * :[-2, -1, 0, 1, 2, 3, 4, 5, 6, 7, 8, 9]
 */
//#define SERIAL_PORT_2 -1
//#define BAUDRATE_2 250000   // :[2400, 9600, 19200, 38400, 57600, 115200, 250000, 500000, 1000000] Enable to override BAUDRATE

/**
 * Select a third serial port on the board to use for communication with the host.
 * Currently supported for AVR, DUE, SAMD51, LPC1768/9, STM32/STM32F1/HC32, and Teensy 4.x
 * :[-1, 0, 1, 2, 3, 4, 5, 6, 7, 8, 9]
 */
//#define SERIAL_PORT_3 1
//#define BAUDRATE_3 250000   // :[2400, 9600, 19200, 38400, 57600, 115200, 250000, 500000, 1000000] Enable to override BAUDRATE

/**
 * Select a serial port to communicate with RS485 protocol
 * :[-1, 0, 1, 2, 3, 4, 5, 6, 7, 8, 9]
 */
//#define RS485_SERIAL_PORT 1
#ifdef RS485_SERIAL_PORT
  //#define M485_PROTOCOL 1   // Check your host for protocol compatibility
  //#define RS485_BUS_BUFFER_SIZE 128
#endif

// Enable the Bluetooth serial interface on AT90USB devices
//#define BLUETOOTH

// Name displayed in the LCD "Ready" message and Info menu
//#define CUSTOM_MACHINE_NAME "3D Printer"

// Printer's unique ID, used by some programs to differentiate between machines.
// Choose your own or use a service like https://www.uuidgenerator.net/version4
//#define MACHINE_UUID "00000000-0000-0000-0000-000000000000"

// @section stepper drivers

/**
 * Stepper Drivers
 *
 * These settings allow Marlin to tune stepper driver timing and enable advanced options for
 * stepper drivers that support them. You may also override timing options in Configuration_adv.h.
 *
 * Use TMC2208/TMC2208_STANDALONE for TMC2225 drivers and TMC2209/TMC2209_STANDALONE for TMC2226 drivers.
 *
 * Options: A4988, A5984, DRV8825, LV8729, TB6560, TB6600, TMC2100,
 *          TMC2130, TMC2130_STANDALONE, TMC2160, TMC2160_STANDALONE,
 *          TMC2208, TMC2208_STANDALONE, TMC2209, TMC2209_STANDALONE,
 *          TMC2660, TMC2660_STANDALONE, TMC5130, TMC5130_STANDALONE,
 *          TMC5160, TMC5160_STANDALONE
 * :['A4988', 'A5984', 'DRV8825', 'LV8729', 'TB6560', 'TB6600', 'TMC2100', 'TMC2130', 'TMC2130_STANDALONE', 'TMC2160', 'TMC2160_STANDALONE', 'TMC2208', 'TMC2208_STANDALONE', 'TMC2209', 'TMC2209_STANDALONE', 'TMC2660', 'TMC2660_STANDALONE', 'TMC5130', 'TMC5130_STANDALONE', 'TMC5160', 'TMC5160_STANDALONE']
 */
#define X_DRIVER_TYPE  TMC5160

#define Y_DRIVER_TYPE  TMC5160
#define Y2_DRIVER_TYPE TMC5160

#define Z_DRIVER_TYPE  TMC2209

//#define X2_DRIVER_TYPE A4988
//#define Z2_DRIVER_TYPE A4988
//#define Z3_DRIVER_TYPE A4988
//#define Z4_DRIVER_TYPE A4988
#define I_DRIVER_TYPE  TMC2209
#define J_DRIVER_TYPE  TMC2209
#define K_DRIVER_TYPE  TMC2209

//munro - the below were on in Printess version
//#define U_DRIVER_TYPE  TMC2209 //commented out to replace with Y2
// #define V_DRIVER_TYPE  TMC2209


//#define W_DRIVER_TYPE  A4988
// #define E0_DRIVER_TYPE A4988
//#define E1_DRIVER_TYPE A4988
//#define E2_DRIVER_TYPE A4988
//#define E3_DRIVER_TYPE A4988
//#define E4_DRIVER_TYPE A4988
//#define E5_DRIVER_TYPE A4988
//#define E6_DRIVER_TYPE A4988
//#define E7_DRIVER_TYPE A4988

/**
 * Additional Axis Settings
 *
 * Define AXISn_ROTATES for all axes that rotate or pivot.
 * Rotational axis coordinates are expressed in degrees.
 *
 * AXISn_NAME defines the letter used to refer to the axis in (most) G-code commands.
 * By convention the names and roles are typically:
 *   'A' : Rotational axis parallel to X
 *   'B' : Rotational axis parallel to Y
 *   'C' : Rotational axis parallel to Z
 *   'U' : Secondary linear axis parallel to X
 *   'V' : Secondary linear axis parallel to Y
 *   'W' : Secondary linear axis parallel to Z
 *
 * Regardless of these settings the axes are internally named I, J, K, U, V, W.
 */
#ifdef I_DRIVER_TYPE
  #define AXIS4_NAME 'A' // :['A', 'B', 'C', 'U', 'V', 'W']
  #define AXIS4_ROTATES
#endif
#ifdef J_DRIVER_TYPE
  #define AXIS5_NAME 'B' // :['B', 'C', 'U', 'V', 'W']
  #define AXIS5_ROTATES
#endif
#ifdef K_DRIVER_TYPE
  #define AXIS6_NAME 'C' // :['C', 'U', 'V', 'W']
  #define AXIS6_ROTATES
#endif
#ifdef U_DRIVER_TYPE
  #define AXIS7_NAME 'U' // :['U', 'V', 'W']
  //#define AXIS7_ROTATES
#endif
#ifdef V_DRIVER_TYPE
  #define AXIS8_NAME 'V' // :['V', 'W']
  //#define AXIS8_ROTATES
#endif
#ifdef W_DRIVER_TYPE
  #define AXIS9_NAME 'W' // :['W']
  //#define AXIS9_ROTATES
#endif

// @section extruder

// This defines the number of extruders
// :[0, 1, 2, 3, 4, 5, 6, 7, 8]
#define EXTRUDERS 0

// Generally expected filament diameter (1.75, 2.85, 3.0, ...). Used for Volumetric, Filament Width Sensor, etc.
#define DEFAULT_NOMINAL_FILAMENT_DIA 4.76

// For Cyclops or any "multi-extruder" that shares a single nozzle.
//#define SINGLENOZZLE

// Save and restore temperature and fan speed on tool-change.
// Set standby for the unselected tool with M104/106/109 T...
#if ENABLED(SINGLENOZZLE)
  //#define SINGLENOZZLE_STANDBY_TEMP
  //#define SINGLENOZZLE_STANDBY_FAN
#endif

// A dual extruder that uses a single stepper motor
//#define SWITCHING_EXTRUDER
#if ENABLED(SWITCHING_EXTRUDER)
  #define SWITCHING_EXTRUDER_SERVO_NR 0
  #define SWITCHING_EXTRUDER_SERVO_ANGLES { 0, 90 } // Angles for E0, E1[, E2, E3]
  #if EXTRUDERS > 3
    #define SWITCHING_EXTRUDER_E23_SERVO_NR 1
  #endif
#endif

// Switch extruders by bumping the toolhead. Requires EVENT_GCODE_TOOLCHANGE_#.
//#define MECHANICAL_SWITCHING_EXTRUDER

/**
 * A dual-nozzle that uses a servomotor to raise/lower one (or both) of the nozzles.
 * Can be combined with SWITCHING_EXTRUDER.
 */
//#define SWITCHING_NOZZLE
#if ENABLED(SWITCHING_NOZZLE)
  #define SWITCHING_NOZZLE_SERVO_NR 0
  //#define SWITCHING_NOZZLE_E1_SERVO_NR 1          // If two servos are used, the index of the second
  #define SWITCHING_NOZZLE_SERVO_ANGLES { 0, 90 }   // A pair of angles for { E0, E1 }.
                                                    // For Dual Servo use two pairs: { { lower, raise }, { lower, raise } }
  #define SWITCHING_NOZZLE_SERVO_DWELL 2500         // Dwell time to wait for servo to make physical move
#endif

// Switch nozzles by bumping the toolhead. Requires EVENT_GCODE_TOOLCHANGE_#.
//#define MECHANICAL_SWITCHING_NOZZLE

/**
 * Two separate X-carriages with extruders that connect to a moving part
 * via a solenoid docking mechanism. Requires SOL1_PIN and SOL2_PIN.
 */
//#define PARKING_EXTRUDER

/**
 * Two separate X-carriages with extruders that connect to a moving part
 * via a magnetic docking mechanism using movements and no solenoid
 *
 * project   : https://www.thingiverse.com/thing:3080893
 * movements : https://youtu.be/0xCEiG9VS3k
 *             https://youtu.be/Bqbcs0CU2FE
 */
//#define MAGNETIC_PARKING_EXTRUDER

#if ANY(PARKING_EXTRUDER, MAGNETIC_PARKING_EXTRUDER)

  #define PARKING_EXTRUDER_PARKING_X { -78, 184 }     // X positions for parking the extruders
  #define PARKING_EXTRUDER_GRAB_DISTANCE 1            // (mm) Distance to move beyond the parking point to grab the extruder

  #if ENABLED(PARKING_EXTRUDER)

    #define PARKING_EXTRUDER_SOLENOIDS_INVERT           // If enabled, the solenoid is NOT magnetized with applied voltage
    #define PARKING_EXTRUDER_SOLENOIDS_PINS_ACTIVE LOW  // LOW or HIGH pin signal energizes the coil
    #define PARKING_EXTRUDER_SOLENOIDS_DELAY 250        // (ms) Delay for magnetic field. No delay if 0 or not defined.
    //#define MANUAL_SOLENOID_CONTROL                   // Manual control of docking solenoids with M380 S / M381

  #elif ENABLED(MAGNETIC_PARKING_EXTRUDER)

    #define MPE_FAST_SPEED      9000      // (mm/min) Speed for travel before last distance point
    #define MPE_SLOW_SPEED      4500      // (mm/min) Speed for last distance travel to park and couple
    #define MPE_TRAVEL_DISTANCE   10      // (mm) Last distance point
    #define MPE_COMPENSATION       0      // Offset Compensation -1 , 0 , 1 (multiplier) only for coupling

  #endif

#endif

/**
 * Switching Toolhead
 *
 * Support for swappable and dockable toolheads, such as
 * the E3D Tool Changer. Toolheads are locked with a servo.
 */
//#define SWITCHING_TOOLHEAD

/**
 * Magnetic Switching Toolhead
 *
 * Support swappable and dockable toolheads with a magnetic
 * docking mechanism using movement and no servo.
 */
//#define MAGNETIC_SWITCHING_TOOLHEAD

/**
 * Electromagnetic Switching Toolhead
 *
 * Parking for CoreXY / HBot kinematics.
 * Toolheads are parked at one edge and held with an electromagnet.
 * Supports more than 2 Toolheads. See https://youtu.be/JolbsAKTKf4
 */
//#define ELECTROMAGNETIC_SWITCHING_TOOLHEAD
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

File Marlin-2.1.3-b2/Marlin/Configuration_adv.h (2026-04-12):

/**
 * Marlin 3D Printer Firmware
 * Copyright (c) 2020 MarlinFirmware [https://github.com/MarlinFirmware/Marlin]
 *
 * Based on Sprinter and grbl.
 * Copyright (c) 2011 Camiel Gubbels / Erik van der Zalm
 *
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
 */
#pragma once

/**
 * Configuration_adv.h
 *
 * Advanced settings.
 * Only change these if you know exactly what you're doing.
 * Some of these settings can damage your printer if improperly set!
 *
 * Basic settings can be found in Configuration.h
 */
#define CONFIGURATION_ADV_H_VERSION 02010300

// @section develop

/**
 * Configuration Export
 *
 * Export the configuration as part of the build. (See signature.py)
 * Output files are saved with the build (e.g., .pio/build/mega2560).
 *
 * See `build_all_examples --ini` as an example of config.ini archiving.
 *
 *  1 = marlin_config.json - Dictionary containing the configuration.
 *      This file is also generated for CONFIGURATION_EMBEDDING.
 *  2 = config.ini - File format for PlatformIO preprocessing.
 *  3 = schema.json - The entire configuration schema. (13 = pattern groups)
 *  4 = schema.yml - The entire configuration schema.
 *  5 = Config.h - Minimal configuration by popular demand.
 */
//#define CONFIG_EXPORT 105 // :[1:'JSON', 2:'config.ini', 3:'schema.json', 4:'schema.yml', 5:'Config.h']

//===========================================================================
//============================= Thermal Settings ============================
//===========================================================================
// @section temperature

/**
 * Thermocouple sensors are quite sensitive to noise.  Any noise induced in
 * the sensor wires, such as by stepper motor wires run in parallel to them,
 * may result in the thermocouple sensor reporting spurious errors.  This
 * value is the number of errors which can occur in a row before the error
 * is reported.  This allows us to ignore intermittent error conditions while
 * still detecting an actual failure, which should result in a continuous
 * stream of errors from the sensor.
 *
 * Set this value to 0 to fail on the first error to occur.
 */
#define THERMOCOUPLE_MAX_ERRORS 15

//
// Custom Thermistor 1000 parameters
//
#if TEMP_SENSOR_0 == 1000
  #define HOTEND0_PULLUP_RESISTOR_OHMS    4700 // Pullup resistor
  #define HOTEND0_RESISTANCE_25C_OHMS   100000 // Resistance at 25C
  #define HOTEND0_BETA                    3950 // Beta value
  #define HOTEND0_SH_C_COEFF                 0 // Steinhart-Hart C coefficient
#endif

#if TEMP_SENSOR_1 == 1000
  #define HOTEND1_PULLUP_RESISTOR_OHMS    4700 // Pullup resistor
  #define HOTEND1_RESISTANCE_25C_OHMS   100000 // Resistance at 25C
  #define HOTEND1_BETA                    3950 // Beta value
  #define HOTEND1_SH_C_COEFF                 0 // Steinhart-Hart C coefficient
#endif

#if TEMP_SENSOR_2 == 1000
  #define HOTEND2_PULLUP_RESISTOR_OHMS    4700 // Pullup resistor
  #define HOTEND2_RESISTANCE_25C_OHMS   100000 // Resistance at 25C
  #define HOTEND2_BETA                    3950 // Beta value
  #define HOTEND2_SH_C_COEFF                 0 // Steinhart-Hart C coefficient
#endif

#if TEMP_SENSOR_3 == 1000
  #define HOTEND3_PULLUP_RESISTOR_OHMS    4700 // Pullup resistor
  #define HOTEND3_RESISTANCE_25C_OHMS   100000 // Resistance at 25C
  #define HOTEND3_BETA                    3950 // Beta value
  #define HOTEND3_SH_C_COEFF                 0 // Steinhart-Hart C coefficient
#endif
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

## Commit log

2026-03-28 initial commit
    initial commit
    [MarlinMesh.scad, esp32.csv]
2026-03-30 updates. added test files and some attempts at cura slicing
    cura sliced into 3 layers for some reason
    need to change the E in the cura gcode to A (duh -> spastic)
    [TESTPRINT1.stl, TESTPRINT1_1.stl]
2026-04-12 Primary Upload
    Added ReadMe, Cad and Cura files
    [1.ipt, 12MM_X_AXIS_SHAFT.0009.ipt, 12MM_X_AXIS_SHAFT.ipt, 1mL Barrel Holder.ipt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]

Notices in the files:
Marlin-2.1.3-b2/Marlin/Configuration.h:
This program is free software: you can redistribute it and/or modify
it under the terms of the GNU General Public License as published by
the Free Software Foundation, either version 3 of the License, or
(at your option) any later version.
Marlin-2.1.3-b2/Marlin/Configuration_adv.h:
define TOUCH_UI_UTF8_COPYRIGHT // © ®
